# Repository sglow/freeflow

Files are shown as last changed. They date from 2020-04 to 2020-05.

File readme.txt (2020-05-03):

This project contains hardware design (schematics & layout) and firmware design for a
small PCB used to sense air flow and air pressure.  The intent is to use a 3D printed 
Venturi tube with this board to help with the current Covid-19 medical emergency.
The project has two potential uses:

- Part of a larger ventilator project.  The airflow sensor is a key component of a ventilator
  design.

- Stand alone use for sharing a commercial ventilator among multiple patients.
  One problem with sharing a ventilator between patients is equalizing the flow.
  This sensor can be used inline at each patient to allow the emergency workers 
  to regulate flow using flow valves.

The schematics and layout files here were made using the open source gEDA tools; gschem
for schematic capture and pcb for layout.  These tools can be downloaded here:
   http://www.geda-project.org/

As of 4/6/20 this project is in the early stages.  There have been two revisions of the PCB
(check the git history to see earlier versions).  The main difference is the type of sensors
used to measure the pressure drop across the venturi tube.

Firmware is working but very preliminary.  Things like calibration values are hard coded at
the moment.  It's under active development and changing rapidly.

I'll try to keep this file updated as things progress.

- Steve Glow

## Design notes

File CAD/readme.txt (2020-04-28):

The CAD files here are based on a openscad design (venturi.scad).
The stl files are created from openscad.  
The step files are created by opening the scad file in freecad and exporting as step.

An alternative source of mechanical designs for this sensor is available here:
https://github.com/Burhan-Q/freeflow

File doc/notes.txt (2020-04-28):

Some general notes.  This is just a place for me to keep track of interesting
info on the web.

Interesting page on Wikipedia:
   https://en.wikipedia.org/wiki/Spirometry

Helpful page on USB virtual serial port:
   http://janaxelson.com/usb_virtual_com_port.htm

The linear motor is set up for 1000 cts/in

From RMVS challenge document:
- Must deliver at least 400ml of air in 1.5 sec
  Minimum flow rate is then 267 ml/sec

  Googling around a bit suggests that most ventilators 
  have a maximum flow rate of 60 to 120 L/min.
  That would be 1000 to 2000 ml/sec

  Max pressures are in the 40cmH2O region

  I found a calculator to calculate TV based on patient size.
  https://www.mdcalc.com/endotracheal-tube-ett-depth-tidal-volume-calculator

  It gives two values, 6mL/Kg and 8mL/Kg

  6' male: 468 - 624mL
  5' male: 300 - 400
  5' female: 276 - 368
  4' female: same as 5'

Important display, pressure on x-axis, tidal volume on y

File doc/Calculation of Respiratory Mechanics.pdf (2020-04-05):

## Calculation of Respiratory Mechanics

# Introduction:

Respiratory mechanics refers to the expression of lung function through measures of pressure and flow. They are very useful to know the status of the lungs of ventilated patients. Below is the screen shot of Hamilton Medical ventilator monitoring menu. This document will try to calculate as much as possible parameters from this menu, using data input from our flow meter and pressure sensor. This should be noted that this is a developing document and will be updated periodically

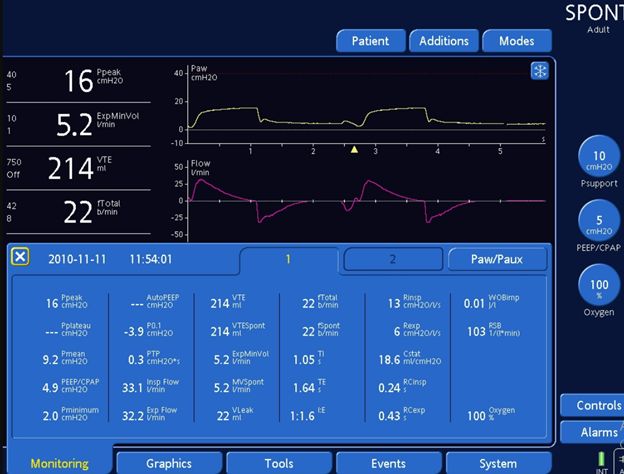
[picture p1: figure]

# 1) Alveolar Pressure:

For volume control setup like ours it’s calculated by

Palv = VT/CRS + PEEP.

VT <= set by us

PEEP<=set by us

CRS= calculated by Equation 6

# 2) Plateau Pressure

There are two methods to calculated it,

1) one is by holding the breath after inspiration for 0.5-1 second and measuring the pressure at inspiratory limb. This will be difficult in our setup of multiple patient.
2) The second method is using below equation and no hold breath maneuver is needed.

VT=tidal volume, set by us

PIP=peak inspiratory pressure , given by our pressure senor

PEEP=set by us

Time constant TE

is calculated by slope of expiratory flow curve between 0.1-0.5 seconds as shown below

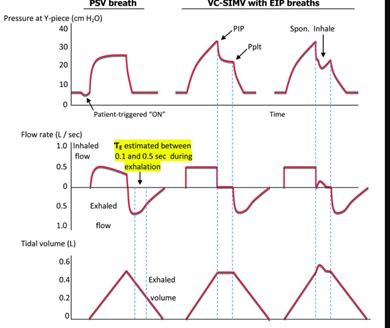
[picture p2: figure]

# 3) Auto-PEEP or iPEEP

Once again it can be calculated by two methods

a) Holding a breath after expiration and waiting for 0.5-1 second and measure pressing at proximal airway is Auto-PEEP, probably not applied in our case
b) It can also be calculated by mathematical equation

VT=tidal volume

CRS as calculated by equation-6

Kx=1/TE, and for TE see equation 2

# 4) Mean Airway Pressure

Calculated using following equation

PIP is peak inspiratory pressure

PEEP is known

TI

is time taken by respiration (SET BY US)

Ttot

total breathing cycle time

# 5) Respiratory System Compliance:

Defined in change in volume of respiratory system per unit of pressure

VT

=tidal volume

Pplat = See equation 2

PEEP=set by us

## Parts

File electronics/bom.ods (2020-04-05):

Item | Qty/board | Manufacturer | Part Number | Description | Value | Reference | Cost
1 | 1 | ST | STM32L412KBT6 | Processor |  | U1 | 2.46
2 | 1 | TI | TPS7B6933QDCYRQ1 | Linear regulator |  | U2 | 0.95
3 | 1 | JAE | DX4R005JJ2R1800 | Connector |  | J2 | 0.62
4 | 1 | Wurth | 150060VS75000 | LED | green | D3 | 0.11
5 | 1 | Wurth | 150060RS75000 | LED | red | D4 | 0.11
6 | 1 | CUI | CMT-0525-75-SMT-TR | Buzzer |  | U3 | 1.47
7 | 1 | Yageo | CC0603KRX7R9BB102 | Capacitor | 1nF | C3 | 0.01
8 | 1 | NXP | MP3V5004DP | Pressure sensor |  | U4
9 | 1 | NKK | A11JP | Switch |  | S2
10 | 2 | Yageo | RC0603FR-07150RL | Resistor | 150 | R1,R4 | 0.01
11 | 1 | Honeywell | MPRLS0001PG0000SA | Pressure sensor |  | U5 | 5.45
12 | 1 | E-switch | 800AWSP9M2QE | Push button |  | S3 | 2.41
13 | 4 | Toshiba | CUS10S30,H3F | Diode |  | D1,D5,D6,D7 | 0.1
14 | 1 | Nexperia | 74HC2G14GV,125 | Inverter |  | U7 | 0.21
15 | 1 | Yageo | CC0603KPX7R9BB103 | Capacitor | 0.01uF | C11 | 0.01
16 | 7 | Yageo | CC0603KRX7R8BB104 | Capacitor | 0.1uF | C12,C4,C5,C6,C7,C8,C9 | 0.01
17 | 1 | Samsung | CL10A105KP8NNNC | Capacitor | 1uF | C13 | 0.01
18 | 1 | Bourns | PEC12R-4222F-S0024 | Encoder |  | U8 | 0.8
19 | 1 | Hirose | DF13-2P-1.25DS(50) | Connector |  | J1 | 0.3
20 | 1 | Diodes Inc | DMN63D8LDW-7 | FET |  | Q1 | 0.1
21 | 1 | Hirose | DF13-4P-1.25DSA | Connector |  | J3 | 0.4
22 | 1 | Sullins | PPTC041LFBN-RC | Connector |  | J4 | 0.32
23 | 1 | Honeywell | HIH8120-021-001 | Humidity sensor |  | U6
24 | 1 | Molex | 705530003 | Connector |  | J5 | 0.8
25 | 8 | Yageo | RC0603FR-0710KL | Resistor | 10k | R10,R2,R3,R5,R6,R7,R8,R9 | 0.01
26 | 2 | Samsung | CL21A106KOQNNNG | Capacitor | 10uF | C1,C2 | 0.03

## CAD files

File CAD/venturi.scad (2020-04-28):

// This file describes the geometry of the freeflow venturi tube.
// I have tried to document the various parameters, most of which can be
// changed to adjust tube geometry.
//
// These are just openscad special variables related to rendering.
// They define how many fascets in an arc.  I have them set for pretty high 
// resolution (slow) rendering.  Making these bigger produces faster but 
// rougher renderings
$fa = 1;      // Minimum angle fragment
$fs = .1;     // Minimum size of a fragment

// M for margin.  I use this to make things overlap slightly for better rendering
M = .01;

// These dimensions describe the PCB that sits on top of the venturi
pcb_length = in2mm(3);
pcb_width  = in2mm(1);

// These are the X axis offsets of the two pressure sensors from the end of the pcb.
// The sensors are both centered in the Y axis, so I don't include that here.
// These values are correct for the rev-2 freeflow board.
pcb_tap_outer  = in2mm(0.3);
pcb_tap_center = in2mm(1.6);

// Tubing that connects to the venturi outer & inner diameter
tube_od = 22;
tube_id = 15;

// Amount that my venturi will overlap the tube on the enterence.
// I'm using a female enterence and male exit
tube_overlap = 10;

// Thickness of the wall of the overlapping section
overlap_thickness = 1.25;

// The outer diameter of the venturi tube enterence will be the 
// same as the tube_id.  The throat diameter is the inner diameter
// of the constricted throat of the venturi.  Smaller gives larger
// readings, especially at low flow rates, but also causes more
// pressure drop through the tube.
throat_d = tube_id * 0.4;
echo( "throat_d ", throat_d );

// These angles define how quickly the venturi will narrow on 
// both entry and exit.  Angles are relative to the center line
// running through the tube.  These angles are pretty typical for
// venturi tubes according to my research.
angle_entry = 12;
angle_exit = 7;

// The exit of the venturi will have the same inner/outer diameter 
// as the tube that attaches to the entry.  I'm assuming that a fitting
// sized for that tube will be connected to the exit end
exit_id = tube_id;
exit_od = tube_od;

// Find the entry and exit distance based on the change of diameter
// and the angles.  
Lnarrow = (tube_id - throat_d)/2 / tan(angle_entry);
Lexpand  = (exit_id - throat_d)/2 / tan(angle_exit);

// This is the length of the exit section.  The fitting attached to the 
// end of the venturi will overlap by up to this much
exit_overlap = 10;

// The length of the throat section is customarily the same as the
// throat diameter
Lthroat = throat_d;

// The length of the enterence to the venturi (before it starts to narrow)
// The outer tap is located in this area, so this is somewhat dictated by the PCB dimensions

pcb_dtap = pcb_tap_center - pcb_tap_outer;
if( pcb_dtap < Lnarrow + Lthroat/2 )
   echo( "<b>ERROR - PCB spacing is too small for this tube!</b>" );
else if( pcb_dtap < Lnarrow + Lthroat/2 + tube_id/2 )
   echo( "<b>Warning - outer tap closer to narrowing then we would like!</b>" );

Lentry = pcb_dtap - Lnarrow - Lthroat/2 + tube_id/2;

// There will be two holes in the side of the tube where we will sense
// pressure.  This is the diameter of those holes
tap_d = 2.5;

VenturiTube();

// This module is the venturi tube itself without the board mount
module VenturiTube()
{
   // This is the Z offset of the bottom of the PCB relative to the bottom of the tube
   pcb_zoff = tube_overlap+Lentry+Lnarrow+Lthroat/2-pcb_tap_center;

   // OK, build the venturi tube.
   difference()
   {
      // This section is the outer shell of the venturi tube.
      union()
      {
         // This is the PCB mount
         hull()
         {
            translate( [tube_od/2+overlap_thickness, -pcb_width/2, pcb_zoff ] )
               cube( [2, pcb_width, pcb_length] );
            translate( [0, -pcb_width/4, pcb_zoff ] )
               cube( [1, pcb_width/2, pcb_length] );
         }

         // This first section is the area in which the venturi tube overlaps
         // the tubing that connects to it.
         cylinder( d=tube_od+2*overlap_thickness, h=tube_overlap );

         // The rest of of the outer shell slowly tapers to the exit outer
         // diameter (which is probably the same as the tube od).  The length
         // is just the sum of all the sections below
         L = Lentry+Lnarrow+Lthroat+Lexpand;
         translate( [0,0,tube_overlap-M] )
            cylinder( d1=tube_od+2*overlap_thickness, d2=exit_od, h=L+M );

         // This last section is the outer part of the section which will fit
         // into the fitting 
         translate( [0,0,tube_overlap+L-M] )
            cylinder( d=exit_od, h=exit_overlap+M );
      }

      // Everything after here is removed from that outer shell.

      // This is the area in which the external tube will enter
      translate( [0,0,-M] ) 
         cylinder( d=tube_od, h=tube_overlap+M );

      // This is the outer section of the venturi.
      // The outer tap will end up in the center of this section.
      translate( [0,0,tube_overlap-M] ) 
         cylinder( d=tube_id, h=Lentry+M );

      // This is the narrowing entry part
      translate( [0,0,tube_overlap+Lentry-M] ) 
         cylinder( d1=tube_id, d2=throat_d, h=Lnarrow+M );

      // This is the throat.  The center tap is in the middle of this
      translate( [0,0,tube_overlap+Lentry+Lnarrow-M] ) 
         cylinder( d=throat_d, h=Lthroat+M );

      // Expanding section
      translate( [0,0,tube_overlap+Lentry+Lnarrow+Lthroat-M] ) 
         cylinder( d1=throat_d, d2=exit_id, h=Lexpand+M );

      // Finally, the section of the venturi which will be overlaped by the exit fitting
      translate( [0,0,tube_overlap+Lentry+Lnarrow+Lthroat+Lexpand-M] ) 
         cylinder( d=exit_id, h=exit_overlap+2*M );

      // Add a hole for the outer pressure sensor tap
      translate( [0,0,pcb_zoff+pcb_tap_outer] )
         rotate( [0,90,0] ) cylinder( d=tap_d, h=tube_od );

      // And center tap
      translate( [0,0,pcb_zoff+pcb_tap_center] )
         rotate( [0,90,0] ) cylinder( d=tap_d, h=tube_od );

      // Hollow out an area below the PCB to allow for through hole parts that might
      // be sticking through.  I should parameterize this better
      translate( [tube_od/2+overlap_thickness+1+M, -pcb_width/2+1, pcb_zoff+1 ] )
         cube( [1, pcb_width-7, pcb_length-7] );
      translate( [tube_od/2+overlap_thickness+1+M, -pcb_width/2+6, pcb_zoff+6 ] )
         cube( [1, pcb_width-7, pcb_length-7] );

      // Add holes for the mounting screws.
      // I'm using brass heat-set inserts in these holes.
      // McMaster-Carr part number 94459A120
      translate( [tube_od/2+overlap_thickness+2,in2mm(0.375),pcb_zoff+in2mm(0.125)] )
         rotate( [0,90,0] ) cylinder( d=3.25, h=8, center=true);
      translate( [tube_od/2+overlap_thickness+2,-in2mm(0.375),pcb_zoff+pcb_length-in2mm(0.125)] )
         rotate( [0,90,0] ) cylinder( d=3.25, h=8, center=true);

      // Cutouts for o-rings (McMaster-Carr 2418T111)
      translate( [tube_od/2+overlap_thickness+2, 0, pcb_zoff+pcb_tap_outer ] )
         rotate( [0,90,0] ) cylinder( d=6.5, h=7, center=true );
      translate( [tube_od/2+overlap_thickness+2, 0, pcb_zoff+pcb_tap_center ] )
         rotate( [0,90,0] ) cylinder( d=6.5, h=7, center=true );
   }
}

function in2mm(x) = x*25.4;

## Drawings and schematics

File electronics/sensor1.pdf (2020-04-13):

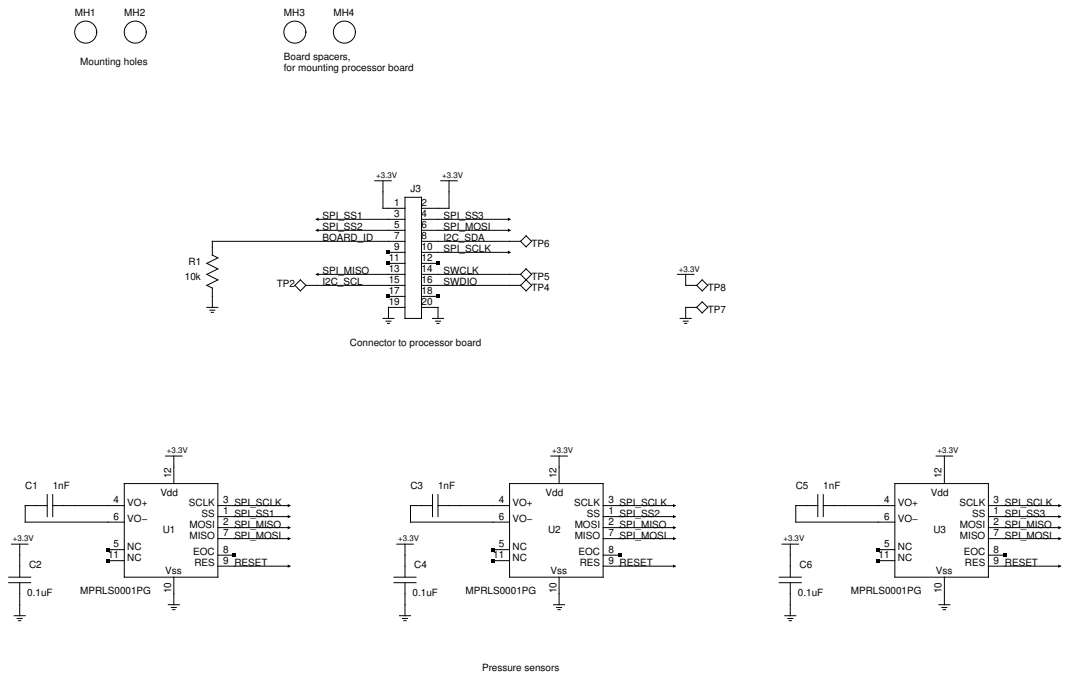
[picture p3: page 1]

Board spacers,
for mounting processor board

Connector to processor board

TITLE Freeflow sensor board

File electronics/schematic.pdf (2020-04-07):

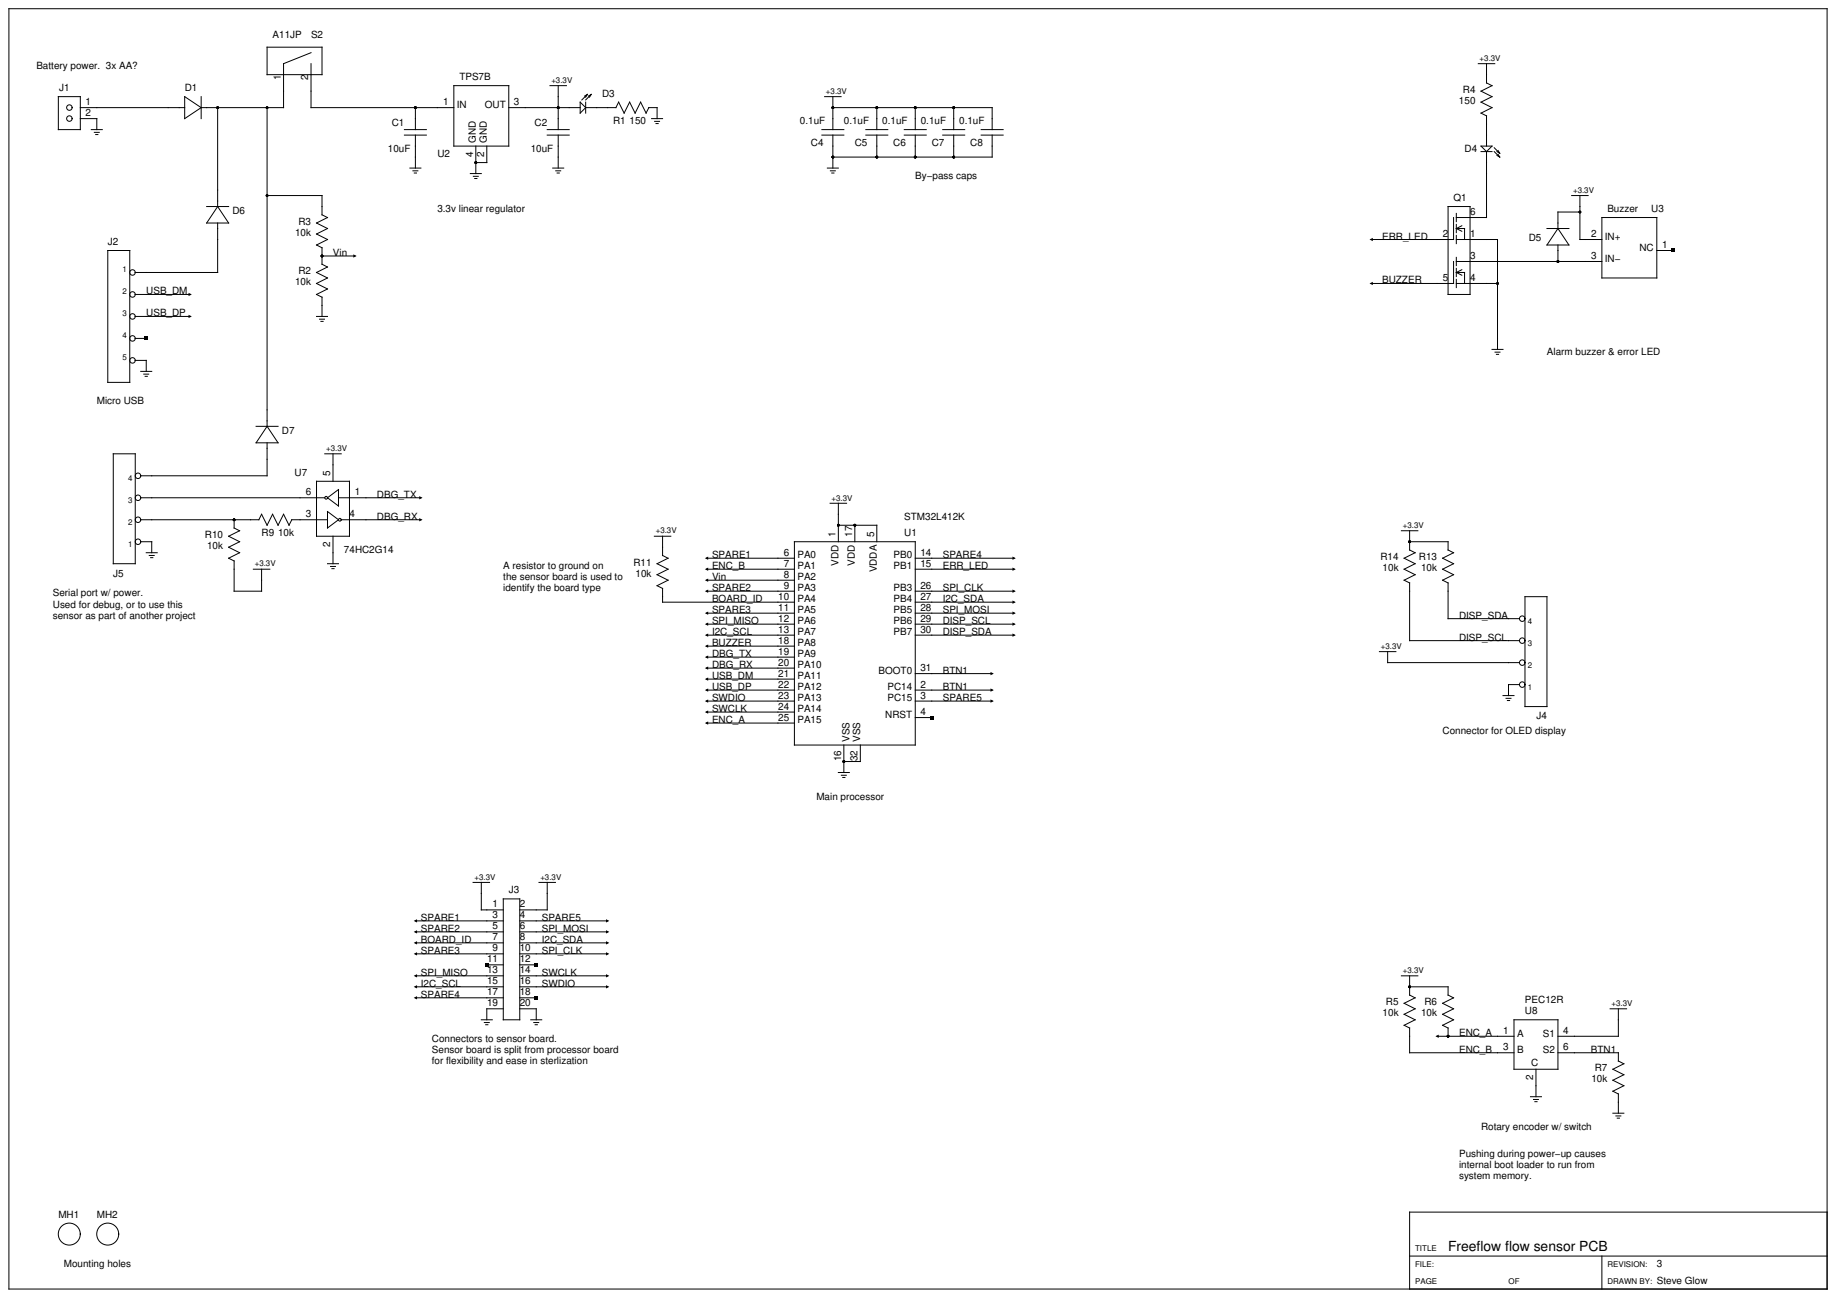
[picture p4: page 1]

Alarm buzzer & error LED

A resistor to ground on
the sensor board is used to
identify the board type

Serial port w/ power.
Used for debug, or to use this
sensor as part of another project

Connector for OLED display

Connectors to sensor board.
Sensor board is split from processor board
for flexibility and ease in sterlization

Pushing during power−up causes
internal boot loader to run from
system memory.

Freeflow flow sensor PCB

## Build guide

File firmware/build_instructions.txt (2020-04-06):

This firmware is being developed on a Linux machine using tools from
the Linux repository.  It's currently being developed on Ubuntu 18.04
although the specific Linux version shouldn't really matter.

No IDE is being used here, files are edited using a text editor and
built from the command line.

The build system is based on scons (see scons.org for details).
To install this in a Debian based Linux system like Ubuntu:
   sudo apt install scons

To build the firmware, just enter 
   scons

The compiler I'm using is straight out of the Ubuntu repositories.
It can be installed using the command:

   sudo apt install gcc-arm-none-eabi

I think that will pull in everything needed (assembler, linker, etc)
Please let me know if I've missed anything.

Once the firmware is built, start the board up running the internal 
boot loader and use the bootloader.py script to flash it.

Steve Glow
sglow@embeddedintelligence.com

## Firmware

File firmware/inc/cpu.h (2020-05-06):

/* cpu.h */

#ifndef _DEF_INC_CPU
#define _DEF_INC_CPU

#include <stdint.h>

#define CLOCK_RATE_MHZ  80
#define CLOCK_RATE      (CLOCK_RATE_MHZ * 1000000)

// Flash memory start/size
#define FLASH_START        0x08000000
#define FLASH_SIZE         0x00020000
#define FLASH_PAGE_LEN     0x00000800

#define MAIN_FW_START      0x08004000
#define MAIN_FW_END        0x08018000

// Interrupt vectors.  These are the offset of the interrupt in the 
// vector table divided by 4
// The interrupt vector table can be found in the reference manual 
// in the section on the NVIC (12)
#define INT_VECT_DMA1_6    0x80/4
#define INT_VECT_TMR15     0xA0/4
#define INT_VECT_TMR16     0xA4/4
#define INT_VECT_SPI1      0xCC/4
#define INT_VECT_UART1     0xD4/4
#define INT_VECT_I2C1      0xBC/4

typedef volatile uint64_t LREG;
typedef volatile uint32_t REG;
typedef volatile uint16_t SREG;
typedef volatile uint8_t  BREG;

// Reset & clock controller
#define RCC_BASE                    0x40021000
typedef struct
{
   REG clkCtrl;                  // 0x00 clock control register (RCC_CR)
   REG clkCal;                   // 0x04 Internal clock sources calibration register (RCC_ICSCR)
   REG clkCfg;                   // 0x08 clock configuration register (RCC_CFGR)
   REG pllCfg;                   // 0x0C PLL configuration register (RCC_PLLCFGR)
   REG pllSaiCfg;                // 0x10 PLLSAI1 configuration register (RCC_PLLSAI1CFGR)
   REG rsvd1;
   REG clkIntEna;                // 0x18 Clock interrupt enable register ( RCC_CIER) 
   REG clkIntFlg;                // 0x1C Clock interrupt flag register ( RCC_CIFR)
   REG clkIntClr;                // 0x20 Clock interrupt clear register ( RCC_CICR)
   REG rsvd2;
   REG periphReset[8];           // 0x28 peripheral reset registers
   REG periphClkEna[8];          // 0x48 peripheral clock registers
   REG sleepClkEna[8];           // 0x68 Clock enable in sleep
   REG indClkCfg;                // 0x88 Peripherals independent clock configuration register (RCC_CCIPR)
   REG rsvd3;
   REG backup;                   // 0x90 Backup domain control register (RCC_BDCR)
   REG status;                   // 0x94 control & status register (RCC_CSR)
   REG recovery;                 // 0x98 Clock recovery RC register (RCC_CRRCR)
   REG indClkCfg2;               // 0x9C Peripherals independent clock configuration register (RCC_CCIPR2)
} RCC_Regs;

// Clock recovery system
#define CRS_BASE                    0x40006000
typedef struct
{
   REG ctrl;
   REG config;
   REG status;
   REG intClr;
} CRS_Regs;

// Interrupt controller
#define NVIC_BASE                   0xE000E100
typedef struct
{
   REG  setEna[32];
   REG  clrEna[32];
   REG  setPend[32];
   REG  clrPend[32];
   REG  active[64];
   BREG priority[1024];
} IntCtrl_Regs;

// System control registers
#define SYSCTL_BASE                 0xE000E000
typedef struct
{
   REG rsvd0;                    // 0xE000E000
   REG intType;                  // 0xE000E004
   REG auxCtrl;                  // 0xE000E008
   REG rsvd1;                    // 0xE000E00C
   REG systick[3];               // 0xE000E010
   REG rsvd2[57];
   REG nvic[768];                // 0xE000E100
   REG cpuid;                    // 0xE000ED00
   REG intCtrl;                  // 0xE000ED04
   REG vtable;                   // 0xE000ED08
   REG apInt;                    // 0xE000ED0C
   REG sysCtrl;                  // 0xE000ED10
   REG cfgCtrl;                  // 0xE000ED14
   REG sysPri[3];                // 0xE000ED18
   REG sysHdnCtrl;               // 0xE000ED24
   REG faultStat;                // 0xE000ED28
   REG hardFaultStat;            // 0xE000ED2C
   REG rsvd3;
   REG mmFaultAddr;              // 0xE000ED34
   REG faultAddr;                // 0xE000ED38
   REG rsvd4[19];
   REG cpac;                     // 0xE000ED88
} SysCtrl_Reg;

// Power controller
#define POWER_BASE                  0x40007000
typedef struct
{
   REG ctrl[4];
   REG status[2];
   REG statClr;
   struct
   {
      REG up;
      REG dn;
   } pull[6];
} PwrCtrl_Reg;

// Digital I/O
#define DIGIO_A_BASE                0x48000000
#define DIGIO_B_BASE                0x48000400
#define DIGIO_C_BASE                0x48000800
typedef struct
{
   REG  mode;
   REG  outType;
   REG  outSpeed;
   REG  pullUpDn;
   REG  inDat;
   REG  outDat;
   SREG set;
   SREG clr;
   REG  lock;
   REG  alt[2];
   REG  reset;
} GPIO_Regs;

#define UART1_BASE                  0x40013800
#define UART2_BASE                  0x40004400
#define UART3_BASE                  0x40004800
#define UART4_BASE                  0x40004C00
typedef struct
{
   REG ctrl[3];
   REG baud;
   REG guard;
   REG timeout;
   REG request;
   REG status;
   REG intClear;
   REG rxDat;
   REG txDat;
} UART_Regs;

#define ADC_BASE                   0X50040000
typedef struct
{
   // A/D specific registers (0x100 total length)
   struct
   {
      REG stat;                  // 0x00 - interrupt and status register (ADC_ISR)
      REG intEna;                // 0x04 - interrupt enable register (ADC_IER)
      REG ctrl;                  // 0x08 - control register (ADC_CR)
      REG cfg[2];                // 0x0C - configuration registers
      REG samp[2];               // 0x14 - sampling time registers
      REG rsvd1;
      REG wdog[3];               // 0x20 - watchdog threshold registers
      REG rsvd2;
      REG seq[4];                // 0x30 - Regular sequence registers
      REG data;                  // 0x40 - Regular data register
      REG rsvd3[2];
      REG iSeq;                  // 0x4C - Injected sequence regiseter
      REG rsvd4[4];
      REG offset[4];             // 0x60 - Offset registers
      REG rsvd5[4];
      REG iData[4];              // 0x80 - Injected channel data
      REG rsvd6[4];
      REG wdCfg[2];              // 0xA0 - Watchdog config
      REG rsvd7[2];
      REG diffSel;               // 0xB0 - Differential mode selection
      REG cal;                   // 0xB4 - Calibration factors
      REG rsvd8[18];
   } adc[2];

   // A/D common registers
   REG comStat;                  // 0x300 - Common status
   REG rsvd9;
   REG comCtrl;                  // 0x304 - Common control
   REG comData;                  // 0x308 - Common data
} ADC_Regs;

#define OPAMP_BASE                  0X40007800
typedef struct
{
   REG ctr;                     // 0x00 - Control / status
   REG trim;                    // 0x04 - Offset trim (normal mode)
   REG trimLP;                  // 0x08 - Offset trim (low power mode)
} OpAmpRegs;

#define TIMER1_BASE                 0x40012C00
#define TIMER2_BASE                 0x40000000
#define TIMER3_BASE                 0x40000400
#define TIMER6_BASE                 0x40001000
#define TIMER7_BASE                 0x40001400
#define TIMER15_BASE                0x40014000
#define TIMER16_BASE                0x40014400
typedef struct
{
   REG ctrl[2];
   REG slaveCtrl;
   REG intEna;
   REG status;
   REG event;
   REG ccMode[2];
   REG ccEnable;
   REG counter;
   REG prescale;
   REG reload;
   REG repeat;
   REG compare[4];
   REG deadTime;
   REG dmaCtrl;
   REG dmaAddr;
   REG opt1;
   REG ccMode3;
   REG compare5;
   REG compare6;
   REG opt2;
   REG opt3;
} TimerRegs;

#define FLASH_BASE                 0x40022000
typedef struct
{
   REG access;
   REG pdKey;
   REG key;
   REG optKey;
   REG status;
   REG ctrl;
   REG ecc;
   REG rsvd1;
   REG option;
   REG pcropStart;
   REG pcropEnd;
   REG wrpA;
   REG wrpB;
} FlashReg;

#define DMA1_BASE                  0x40020000
#define DMA2_BASE                  0x40020400
typedef struct
{
   REG intStat;
   REG intClr;
   struct
   {
      REG config;
      REG count;
      REG pAddr;
      REG mAddr;
      REG rsvd;
   } channel[7];
   REG rsvd[5];
   REG chanSel;
} DMA_Reg;

#define SPI1_BASE                  0x40013000
#define SPI2_BASE                  0x40003800
#define SPI3_BASE                  0x40003C00
typedef struct
{
   REG ctrl[2];
   REG status;
   REG data;
   REG crcPoly;
   REG rxCRC;
   REG txCRC;
} SPI_Regs;

#define I2C1_BASE                  0x40005400
#define I2C2_BASE                  0x40005800
#define I2C3_BASE                  0x40005c00
#define I2C4_BASE                  0x40008400
typedef struct
{
   REG ctrl[2];
   REG addr[2];
   REG timing;
   REG timeout;
   REG status;
   REG intClr;
   REG pec;
   REG rxData;
   REG txData;
} I2C_Regs;

#define CRC_BASE                   0x40023000
typedef struct
{
   REG data;
   REG scratch;
   REG ctrl;
   REG rsvd;
   REG init;
   REG poly;
} CRC_Regs;

#define USBFS_BASE                 0x40006800
typedef struct
{
   REG endpoint[8];                // 0x00 - USB endpoint n register (USB_EPnR)
   REG rsvd[8];
   REG ctrl;                       // 0x40 - USB control register (USB_CNTR)
   REG status;                     // 0x44 - USB interrupt status register (USB_ISTR)
   REG frame;                      // 0x48 - USB frame number register (USB_FNR)
   REG addr;                       // 0x4C - USB device address (USB_DADDR)
   REG btable;                     // 0x50 - Buffer table address (USB_BTABLE)
   REG lpm;                        // 0x54 - LPM control and status register (USB_LPMCSR)
   REG battery;                    // 0x58 - Battery charging detector (USB_BCDR)
} USB_Regs;

#define USB_SRAM_BASE              0x40006C00
typedef struct
{
   SREG txAddr;                    // 0x00 - Transmission buffer address n (USB_ADDRn_TX)
   SREG txCount;                   // 0x02 - Transmission byte count n (USB_COUNTn_TX)
   SREG rxAddr;                    // 0x04 - Reception buffer address n (USB_ADDRn_RX)
   SREG rxCount;                   // 0x06 - Reception byte count n (USB_COUNTn_RX)
} USB_TblEntry;

// inline functions
#define GPIO_MODE_INPUT    0
#define GPIO_MODE_OUTPUT   1
#define GPIO_MODE_ALT      2
#define GPIO_MODE_ANALOG   3
static inline void GPIO_PinMode( uint32_t bank, int pin, int mode )
{
   GPIO_Regs *gpio = (GPIO_Regs *)bank;
   gpio->mode &= ~(3 << (pin*2));
   gpio->mode |= (mode << (pin*2));
}

#define GPIO_OUTTYPE_PUSHPULL   0
#define GPIO_OUTTYPE_OPENDRIAN  1
static inline void GPIO_OutType( uint32_t bank, int pin, int drain )
{
   GPIO_Regs *gpio = (GPIO_Regs *)bank;
   if( drain )
      gpio->outType |=   1<<pin;
   else
      gpio->outType &= ~(1<<pin);
}

static inline void GPIO_PinAltFunc( uint32_t bank, int pin, int func )
{
   GPIO_PinMode( bank, pin, GPIO_MODE_ALT );

   GPIO_Regs *gpio = (GPIO_Regs *)bank;
   int x = (pin<8) ? 0 : 1;
   gpio->alt[x] |= (func << ((pin&7)*4));
}

static inline void GPIO_SetPin( uint32_t bank, int pin )
{
   GPIO_Regs *gpio = (GPIO_Regs *)bank;
   gpio->set = (1<<pin);
}

static inline void GPIO_ClrPin( uint32_t bank, int pin )
{
   GPIO_Regs *gpio = (GPIO_Regs *)bank;
   gpio->clr = (1<<pin);
}

static inline int GPIO_GetPin( uint32_t bank, int pin )
{
   GPIO_Regs *gpio = (GPIO_Regs *)bank;
   return (gpio->inDat & (1<<pin)) ? 1 : 0;
}

static inline void GPIO_TglPin( uint32_t bank, int pin )
{
   if( GPIO_GetPin( bank, pin ) )
      GPIO_ClrPin( bank, pin );
   else
      GPIO_SetPin( bank, pin );
}

static inline void GPIO_Output( uint32_t bank, int pin, int state )
{
   if( state ) GPIO_SetPin( bank, pin );
   else        GPIO_ClrPin( bank, pin );
   GPIO_PinMode( bank, pin, GPIO_MODE_OUTPUT );
   GPIO_OutType( bank, pin, GPIO_OUTTYPE_PUSHPULL );
}

static inline void GPIO_PullUp( uint32_t bank, int pin )
{
   GPIO_Regs *gpio = (GPIO_Regs *)bank;

   uint32_t x = gpio->pullUpDn & ~(3<<(2*pin));
   x |= 1 << (2*pin);
   gpio->pullUpDn = x;
}

static inline void GPIO_PullDn( uint32_t bank, int pin )
{
   GPIO_Regs *gpio = (GPIO_Regs *)bank;

   uint32_t x = gpio->pullUpDn & ~(3<<(2*pin));
   x |= 2 << (2*pin);
   gpio->pullUpDn = x;
}


// Prototypes
void CPU_Init( void );
void EnableInterrupt( int id, int pri );
void Reset( void );
void SwapMode( void );
int CheckSwap( void );

#endif

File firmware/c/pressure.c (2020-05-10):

/* pressure.c */

#include "adc.h"
#include "autooffset.h"
#include "cpu.h"
#include "errors.h"
#include "loop.h"
#include "main.h"
#include "pressure.h"
#include "store.h"
#include "timer.h"
#include "trace.h"
#include "utils.h"
#include "vars.h"

// The Gauge pressure sensors use an SPI serial interface
// All sensors share the same SPI bus with different chip selects:
//
// PA5 - SS for sensor 1
// PA0 - SS for sensor 2
// PA6 - MISO  
// PB5 - MOSI
// PB3 - CLK

// States for the local state machine
#define STATE_IDLE         0     // Idle, in between readings
#define STATE_READ1H       1     // Waiting to receive high byte from sensor 1
#define STATE_READ1L       2     // Waiting for low byte from sensor 1
#define STATE_READ2H       3     // Waiting for high byte from sensor 2
#define STATE_READ2L       4     // Waiting for low byte from sensor 2

// Various local flags
#define FLG_NEW_READING    0x0001
#define FLG_SAVE_POFF      0x0002

// local functions
static void SelectSensor( int which );
static int SetOffsetTime( VarInfo *info, uint8_t *buff, int len );
static int SetPresOff( VarInfo *info, uint8_t *buff, int len );
static int SetCalData( VarInfo *info, uint8_t *buff, int len );
static int GetCalData( VarInfo *info, uint8_t *buff, int len );
static int GetVarFlow( VarInfo *info, uint8_t *buff, int max );
static int GetP1CmH2O( VarInfo *info, uint8_t *buff, int max );
static int GetP2CmH2O( VarInfo *info, uint8_t *buff, int max );

// local data
static uint16_t isrLastRead;
static uint32_t praw[2];
static int32_t  padj[2];
static uint8_t pressureState;
static uint32_t lastPressureRead;
static VarInfo varPressure[2];
static VarInfo varPoffset[2];
static VarInfo varOffCalc;
static VarInfo varPresCal;
static VarInfo varFlow;
static uint32_t pOff[2];
static uint32_t offSum[2];
static uint32_t flags;
static uint16_t offCalcTime;
static uint16_t offCalcCount;
static float calData[CAL_POINTS];

void InitPressure( void )
{
   // Init some variables
   VarInit( &varPressure[0], VARID_PRESSURE1,   "pressure1", VAR_TYPE_FLOAT, &padj[0], VAR_FLG_READONLY );
   VarInit( &varPressure[1], VARID_PRESSURE2,   "pressure2", VAR_TYPE_FLOAT, &padj[1], VAR_FLG_READONLY );
   VarInit( &varPoffset[0],  VARID_POFF1,       "poff1",     VAR_TYPE_INT32, &pOff[0], 0 );
   VarInit( &varPoffset[1],  VARID_POFF2,       "poff2",     VAR_TYPE_INT32, &pOff[1], 0 );
   VarInit( &varPresCal,     VARID_PCAL,        "prescal",   VAR_TYPE_ARY32, &calData, 0 );
   VarInit( &varOffCalc,     VARID_POFF_CALC,   "poffcalc",  VAR_TYPE_INT16, &offCalcTime, 0 );
   VarInit( &varFlow,        VARID_FLOW,        "flow",      VAR_TYPE_FLOAT, 0, VAR_FLG_READONLY );

   varOffCalc.set = SetOffsetTime;
   varPresCal.set = SetCalData;
   varPresCal.get = GetCalData;
   varPresCal.size = 4*CAL_POINTS;
   varPoffset[0].set = SetPresOff;
   varPoffset[1].set = SetPresOff;
   varFlow.get       = GetVarFlow;
   varPressure[0].get = GetP1CmH2O;
   varPressure[1].get = GetP2CmH2O;
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

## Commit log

2020-03-21 Working on schematic
    [flowmeter.sch]
2020-03-21 Working on it
    [flowmeter.sch]
2020-03-21 Finished first cut of schematic
    [flowmeter.sch]
2020-03-21 Layout nearly done
    [flowmeter.sch]
2020-03-22 Added readme file
    [flowmeter.sch]
2020-03-22 Gerber files used for first rev of the board
2020-03-22 venturi tube CAD files
    [venturi_design_ver001.SLDPRT, venturi_design_ver001.STEP, venturi_design_ver002.SLDPRT, venturi_design_ver003.SLDPRT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]
2020-03-22 Renamed a directory
    [flowmeter.sch]
2020-03-22 Moved CAD files into their own sub-directory
    [venturi_design_ver001.SLDPRT, venturi_design_ver001.STEP, venturi_design_ver002.SLDPRT, venturi_design_ver003.SLDPRT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]
2020-03-22 Added tag Rev 1 board for changeset 5f8bd9517f31
2020-03-26 Added BOM
    [bom.ods]
2020-03-27 New CAD files
    Additional CAD files uploaded
    [TestV5.stl, TestV5.stp, freeflow2.stl, freeflow2.stp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]
2020-03-29 Design updates 2020-03-29
    [venturi_design_ver104.STEP, venturi_design_ver104.STL]
2020-03-30 Early version of firmware. Getting decent results with rev-1 board
2020-03-30 Pressure sensor datasheet
2020-04-05 Working on rev-2 calibration and testing
2020-04-05 Updated board design files for rev-2 PCB
    [bom.ods, flowmeter.sch]
2020-04-05 Added tag Rev-2 PCB files for changeset 97711d333a08
2020-04-07 Working on rev-3 PCB. This version splits the sensors off onto a second board which allows more flexibility with sensor choice and also allows the sensor board to be sterilized indipendent from the m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
    [flowmeter.sch]
2020-04-07 Gerber files from rev-2 board
2020-04-07 Minor touch-ups, changed mounting hole to M2
2020-04-07 Fixed bad refdes for bottom connector
    [flowmeter.sch]
2020-04-07 Added contents to title block
    [flowmeter.sch]
2020-04-07 Sensor board to go with rev-3 PCB
    [sensor1.sch]
2020-04-12 Created a second version of the sensor board using Bosch BMP280 pressure sensors. These are less expensive and more plentiful then the ones I was previously using. Worth testing with
    [sensor2.sch]
2020-04-13 Added pdf version of sensor board
2020-04-28 Replace out of date CAD files with new scad file
    [TestV5.stl, TestV5.stp, freeflow2.stl, freeflow2.stp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]
2020-04-28 Split design into CPU board and sensor board to allow easier testing of different sensors
    [sensor2.sch, sensor3.sch]
2020-04-28 Fixed bad footprint for 20 pin headers. Added gerber files for sensor boards
2020-05-10 Lots of cleanup. Removed support for REV1 boards.
